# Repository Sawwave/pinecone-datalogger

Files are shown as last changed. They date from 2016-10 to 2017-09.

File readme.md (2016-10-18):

Arm based Datalogger running the Atmel SAM D20 MCU.

The Pinecone logger is a specialized, yet inexpensive data logger intended for sensing environmental variables. The ease of use and low cost of these datalogger systems make them ideal for mass deployment over a large area, allowing measurement of spatially-distributed data, rather than just a time-series of one point from a single logger.

The logger supports the following sensors natively:
	DHT-22 Temperature and Humidity sensor
	1 potentiometer implemented as a point dendrometer with 14 bits of precision
	multiple ports supporting sensors implementing the SDI-12 interface, which includes most Decagon brand sensors
	1 sap flow sensor implemented with a heating element and 4 thermocouples.

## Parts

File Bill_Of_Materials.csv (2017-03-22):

Digi-Key Part Number | Manufacturer | Manufacturer Part Number | Customer Reference | Quantity 1 | Quantity 2 | Quantity 3 | Mfg Std Lead Time | Description | Comments | RoHS Status | Lead Free Status | REACH Status
ATSAMD20E18A-AUTCT-ND | MICROCHIP TECHNOLOGY (VA) | ATSAMD20E18A-AUT | MCU | 1 | 0 | 0 | 19 Weeks | IC MCU 32BIT 256KB FLASH 32TQFP |  | RoHS Compliant | Lead free | Unaffected Dec-2015
DS3231SN#T&RCT-ND | MAXIM INTEGRATED (VA) | DS3231SN#T&R | RTC | 1 | 0 | 0 | 6 Weeks | IC RTC CLK/CALENDAR I2C 16-SOIC |  | RoHS Compliant | Lead free | Unaffected Jun-2016
AP2281-3WG-7DICT-ND | DIODES INCORPORATED (VA) | AP2281-3WG-7 | 3V3 LOAD SWITCH | 1 | 0 | 0 | 8 Weeks | IC LOAD SWITCH 100US SOT-26 |  | RoHS Compliant | Lead free | Unaffected Jun-2016
576-2749-1-ND | MICROCHIP TECHNOLOGY (VA) | MIC5211-LXYM6-TR | REGULATOR | 1 | 0 | 0 | 12 Weeks | IC REG LDO 3.3V/5V 80MA SOT23-6 |  | RoHS Compliant | Lead free | Unaffected Jun-2016
MAX4618ESE+-ND | MAXIM INTEGRATED | MAX4618ESE+ | TC MUX | 1 | 0 | 0 | 6 Weeks | IC MULTIPLEXER DUAL 4X1 16SOIC | Alternate Packaging Exists | RoHS Compliant | Lead free | Unaffected Jun-2016
MAX31856MUD+-ND | MAXIM INTEGRATED | MAX31856MUD+ | TC AMP | 1 | 0 | 0 | 14 Weeks | IC CONV THERMOCOUPLE 14TSSOP | Alternate Packaging Exists | RoHS Compliant | Lead free | Unaffected Jun-2016
CP-102A-ND | CUI INC | PJ-102A | PWR JACK | 1 | 0 | 0 | 10 Weeks | CONN PWR JACK 2X5.5MM SOLDER |  | RoHS Compliant | Lead free | Unaffected Jun-2015
952-1389-ND | HARWIN INC | M50-3600542 | CORTEX DEBUG PORT | 1 | 0 | 0 | 10 Weeks | CONN HDR 1.27MM SMD AU 10POS | Alternate Packaging Exists | RoHS Compliant | Lead free | Unaffected Dec-2015
ED10565-ND | ON SHORE TECHNOLOGY INC | OSTVN06A150 | 6 PIN TERM | 4 | 0 | 0 | 8 Weeks | CONN TERM BLOCK 2.54MM 6POS PCB |  | RoHS Compliant | Lead free | Unaffected Jun-2016
HR1964CT-ND | HIROSE ELECTRIC CO LTD (VA) | DM3AT-SF-PEJM5 | SD CARD PORT | 1 | 0 | 0 | 8 Weeks | CONN MICRO SD CARD PUSH-PUSH R/A | Multiple packaging options exist for the part number you requested. This part was selected by the Digi-Key Auto Sensor | RoHS Compliant | Lead free | Not Available
ED10567-ND | ON SHORE TECHNOLOGY INC | OSTVN10A150 | 10 PIN TERM | 1 | 0 | 0 | 8 Weeks | CONN TERM BLOCK 2.54MM 10POS PCB |  | RoHS Compliant | Lead free | Unaffected Jun-2016
490-1691-1-ND | MURATA ELECTRONICS (VA) | GRM21BR71C105KA01L | 1UF CAP | 2 | 0 | 0 | 11 Weeks | CAP CER 1UF 16V X7R 0805 |  | RoHS Compliant | Lead free | Unaffected Jun-2016
399-1170-1-ND | KEMET (VA) | C0805C104K5RACTU | 0.1UF CAP | 13 | 0 | 0 | 22 Weeks | CAP CER 0.1UF 50V X7R 0805 |  | RoHS Compliant | Lead free | Unaffected Jun-2016
490-4735-1-ND | MURATA ELECTRONICS (VA) | GRM219R61A106KE44D | 10UF CAP | 2 | 0 | 0 | 11 Weeks | CAP CER 10UF 10V X5R 0805 |  | RoHS Compliant | Lead free | Unaffected Jun-2016
399-1158-1-ND | KEMET (VA) | C0805C103K5RACTU | 0.01UF CAP | 2 | 0 | 0 | 22 Weeks | CAP CER 10000PF 50V X7R 0805 |  | RoHS Compliant | Lead free | Unaffected Jun-2016
399-9616-1-ND | KEMET (VA) | Z0805C221APMST | FERRITE BEAD | 1 | 0 | 0 | 18 Weeks | FERRITE BEAD 220 OHM 0805 1LN |  | RoHS Compliant | Lead free | Unaffected Jun-2016
785-1014-1-ND | ALPHA & OMEGA SEMICONDUCTOR INC (VA) | AO3420 | N-FET | 2 | 0 | 0 | 16 Weeks | MOSFET N-CH 20V 6A SOT23 |  | RoHS Compliant | Lead free | Unaffected Jun-2016
311-10KARCT-ND | YAGEO (VA) | RC0805JR-0710KL | 10K OHM | 8 | 0 | 0 | 22 Weeks | RES SMD 10K OHM 5% 1/8W 0805 |  | RoHS Compliant | Lead free | Unaffected Dec-2015
311-1.0KARCT-ND | YAGEO (VA) | RC0805JR-071KL | 1K OHM | 1 | 0 | 0 | 22 Weeks | RES SMD 1K OHM 5% 1/8W 0805 | Multiple packaging options exist for the part number you requested. This part was selected by the Digi-Key Auto Sensor | RoHS Compliant | Lead free | Unaffected Dec-2015
311-68ARCT-ND | YAGEO (VA) | RC0805JR-0768RL | 68 OHM | 1 | 0 | 0 | 22 Weeks | RES SMD 68 OHM 5% 1/8W 0805 | Multiple packaging options exist for the part number you requested. This part was selected by the Digi-Key Auto Sensor | RoHS Compliant | Lead free | Unaffected Dec-2015
475-2560-1-ND | OSRAM OPTO SEMICONDUCTORS INC(VA) | LY R976-PS-36 | LED | 1 | 0 | 0 | 10 Weeks | LED YELLOW DIFFUSED 0805 SMD |  | RoHS Compliant | Lead free | Unaffected Dec-2015
952-1662-1-ND | HARWIN INC (VA) | S8201-46R | BATT HOLDER | 1 | 0 | 0 | 10 Weeks | HOLDER BATT COIN 12.5X2.5MM SMD |  | RoHS Compliant | Lead free | Unaffected Dec-2015
P033-ND | PANASONIC - BSG | CR1220 | 3V BATT | 1 | 0 | 0 | 14 Weeks | BATTERY LITHIUM 3V COIN 12.5MM |  | Not applicable | Not applicable | Not Available

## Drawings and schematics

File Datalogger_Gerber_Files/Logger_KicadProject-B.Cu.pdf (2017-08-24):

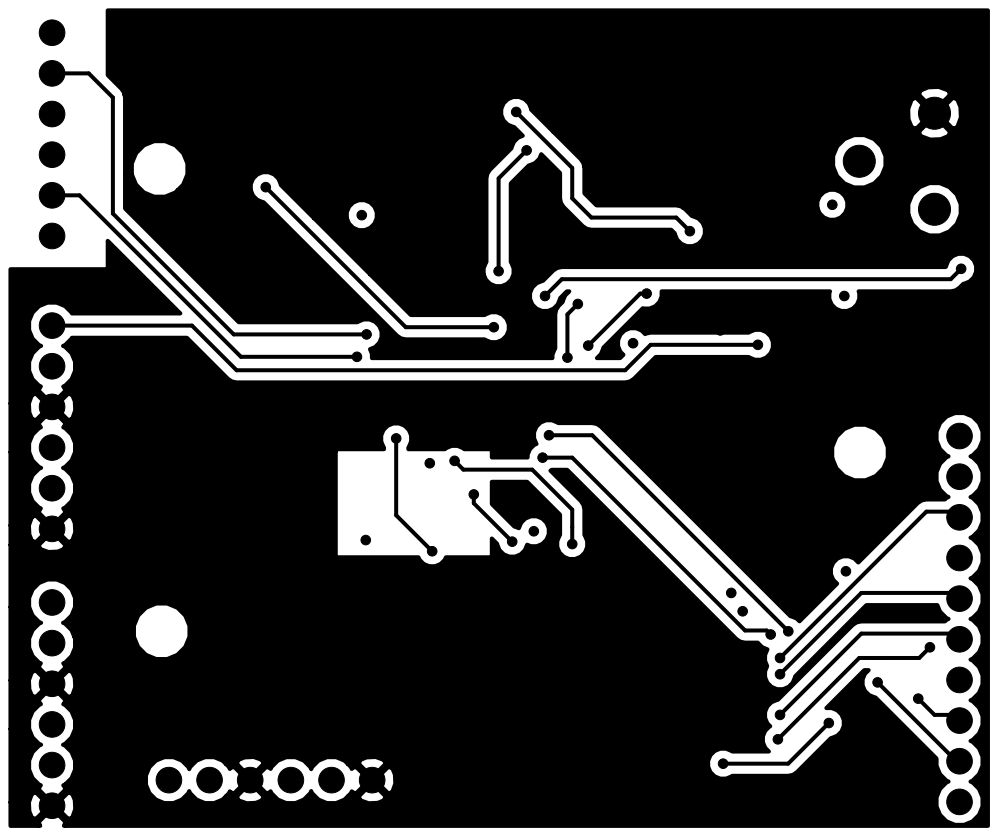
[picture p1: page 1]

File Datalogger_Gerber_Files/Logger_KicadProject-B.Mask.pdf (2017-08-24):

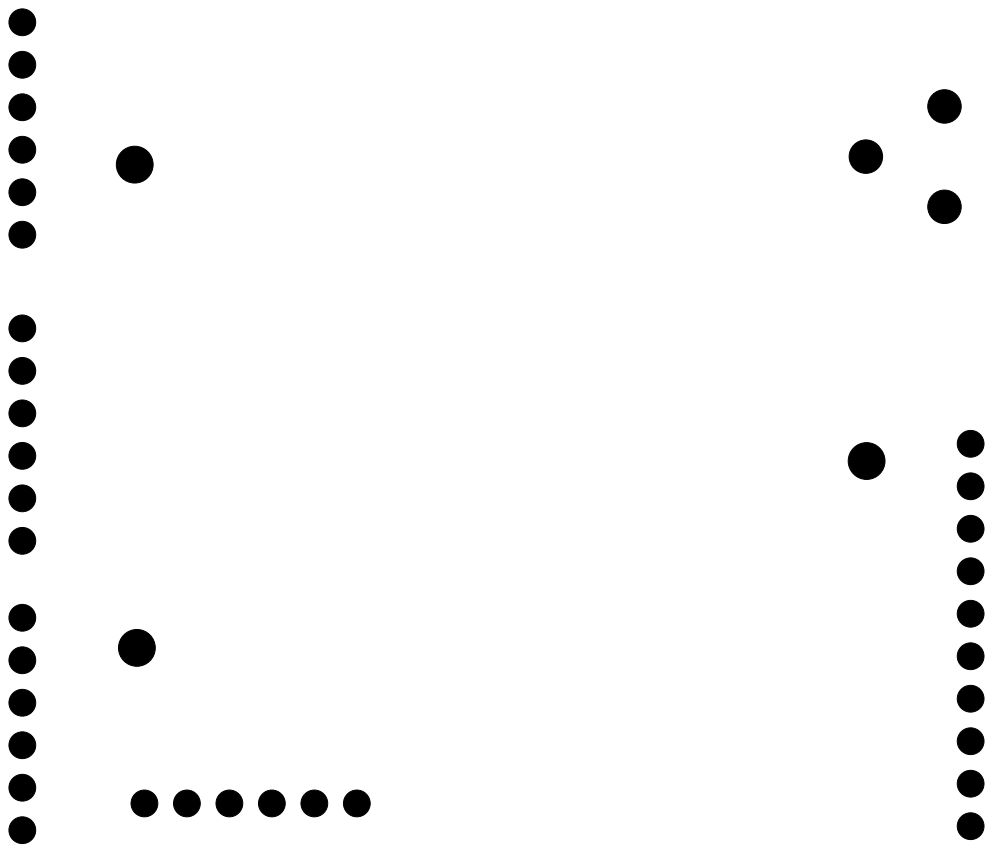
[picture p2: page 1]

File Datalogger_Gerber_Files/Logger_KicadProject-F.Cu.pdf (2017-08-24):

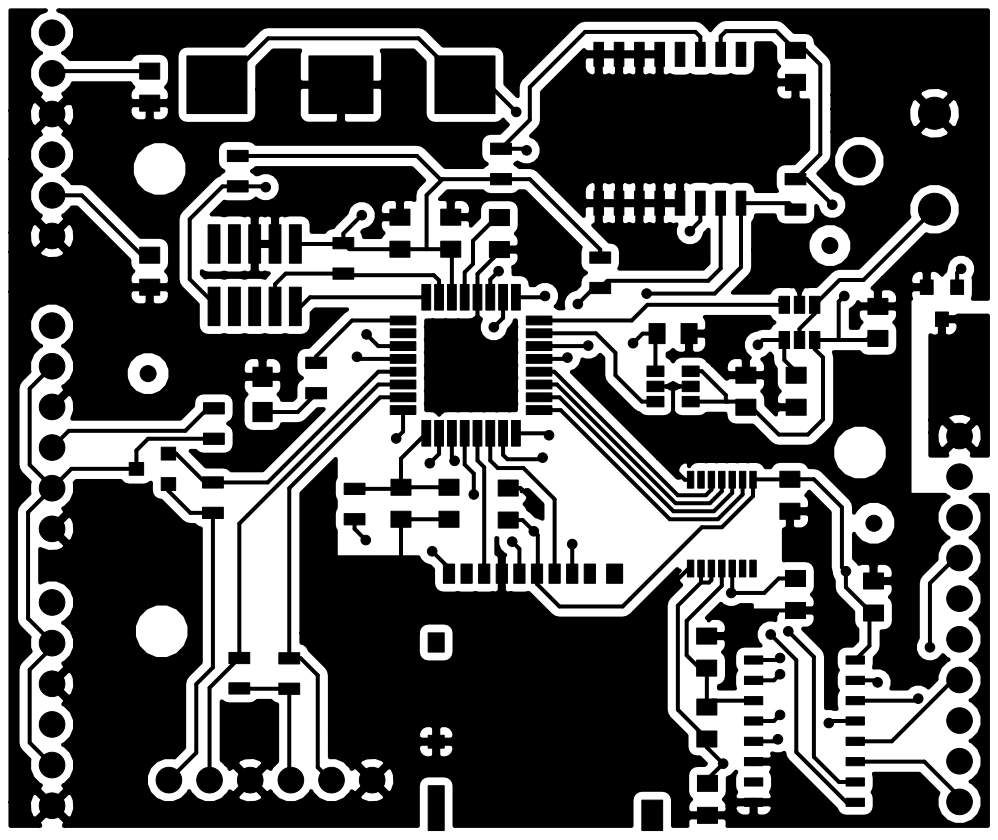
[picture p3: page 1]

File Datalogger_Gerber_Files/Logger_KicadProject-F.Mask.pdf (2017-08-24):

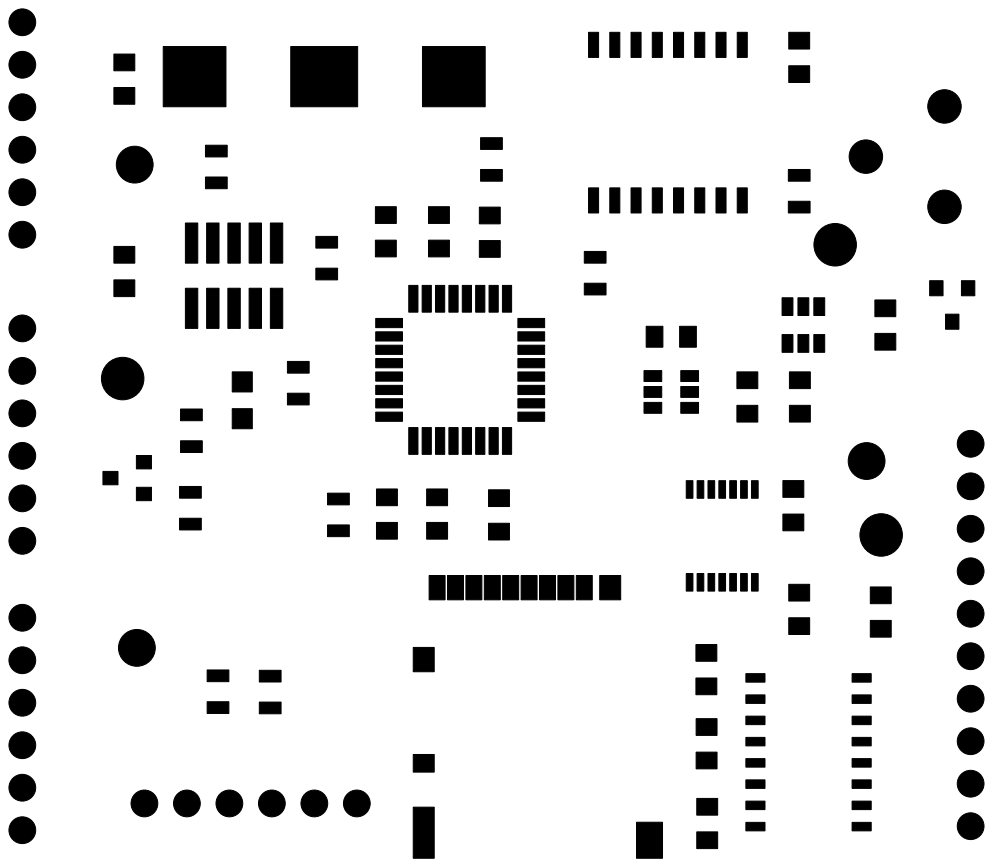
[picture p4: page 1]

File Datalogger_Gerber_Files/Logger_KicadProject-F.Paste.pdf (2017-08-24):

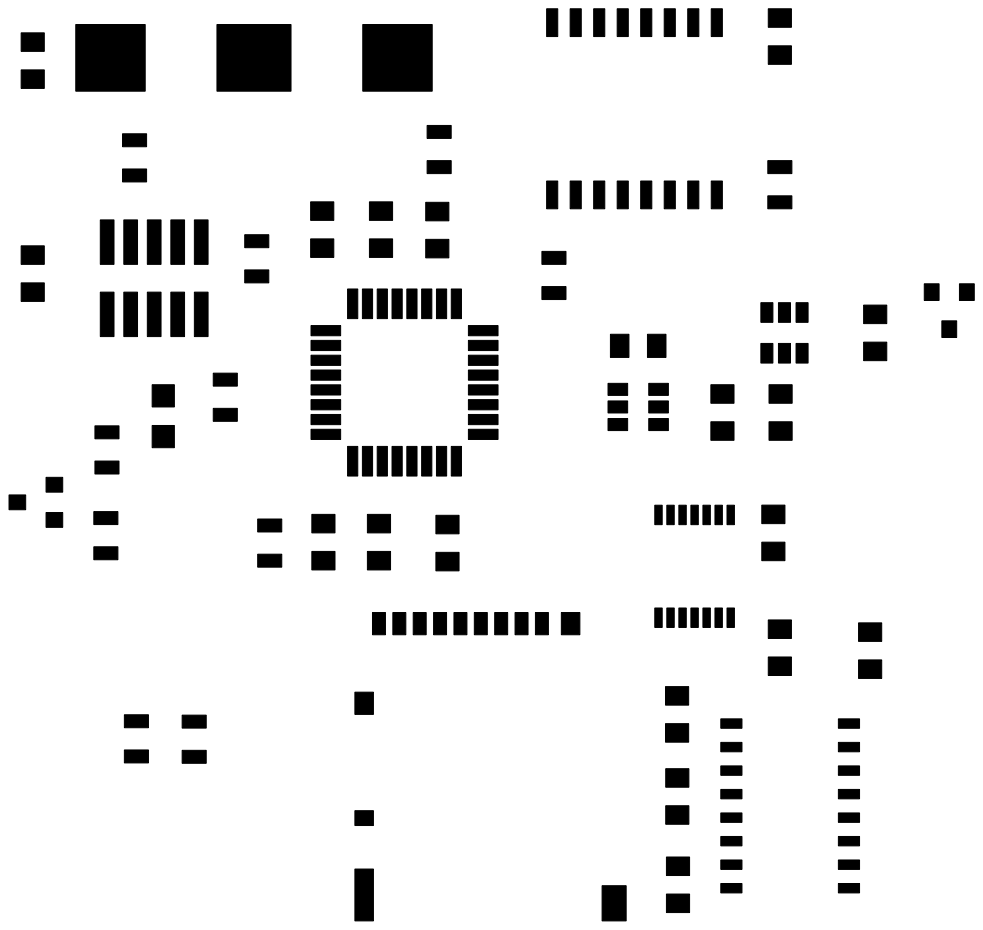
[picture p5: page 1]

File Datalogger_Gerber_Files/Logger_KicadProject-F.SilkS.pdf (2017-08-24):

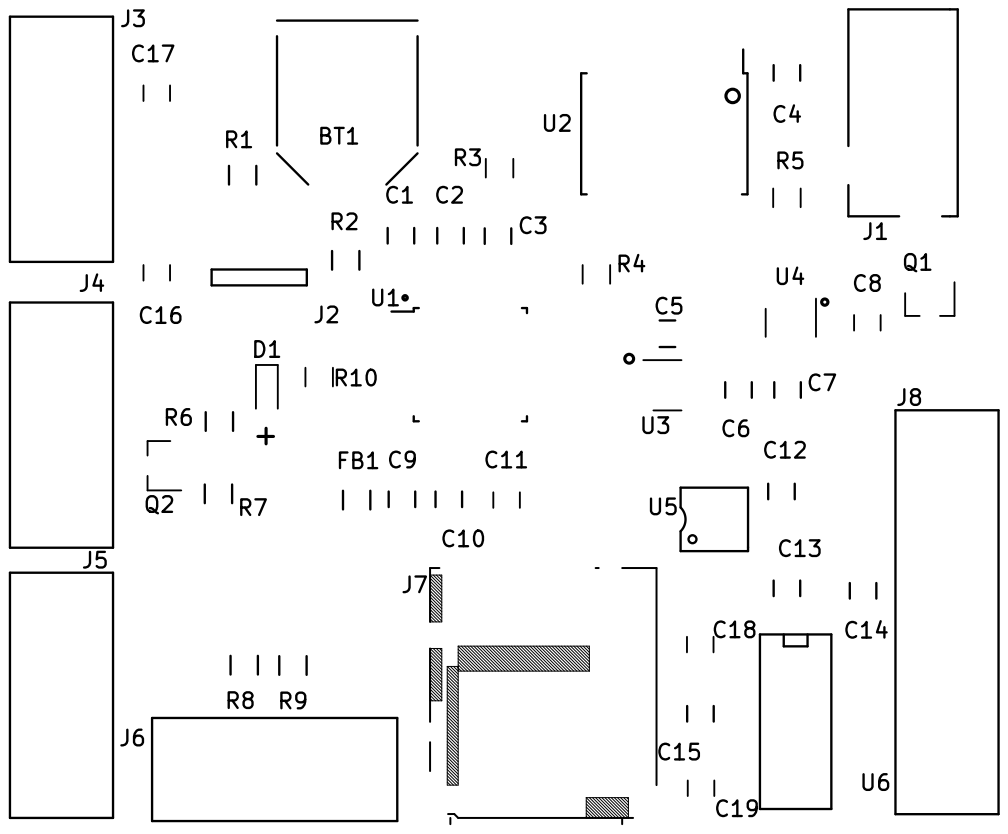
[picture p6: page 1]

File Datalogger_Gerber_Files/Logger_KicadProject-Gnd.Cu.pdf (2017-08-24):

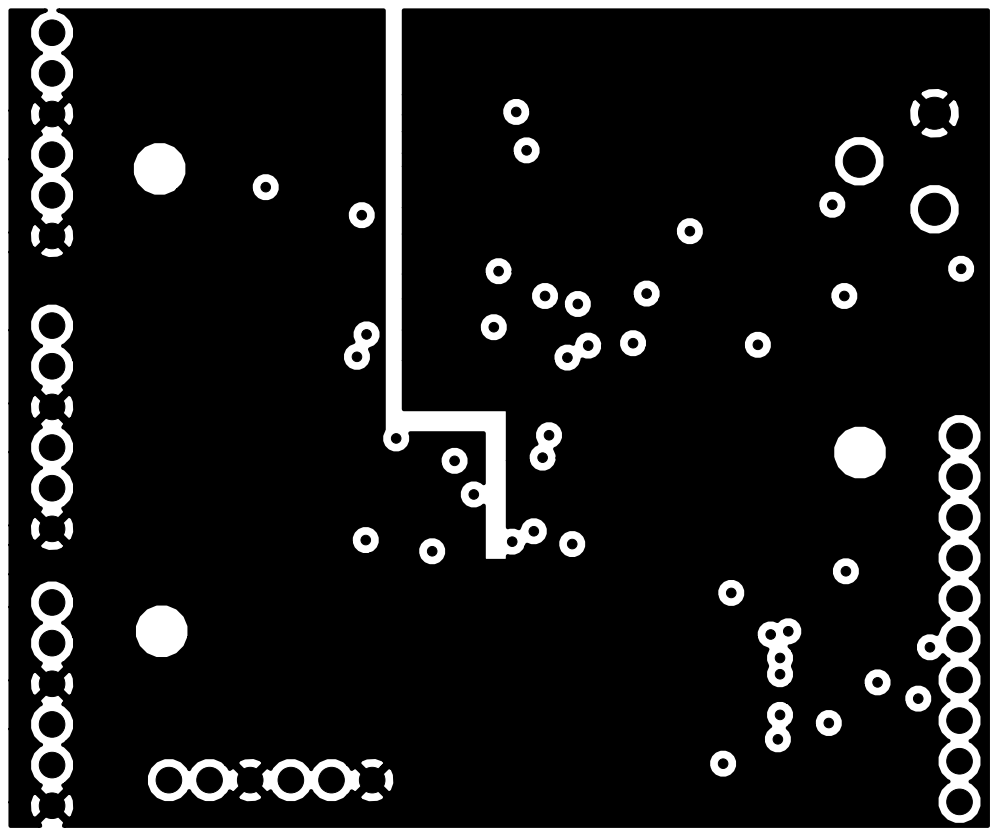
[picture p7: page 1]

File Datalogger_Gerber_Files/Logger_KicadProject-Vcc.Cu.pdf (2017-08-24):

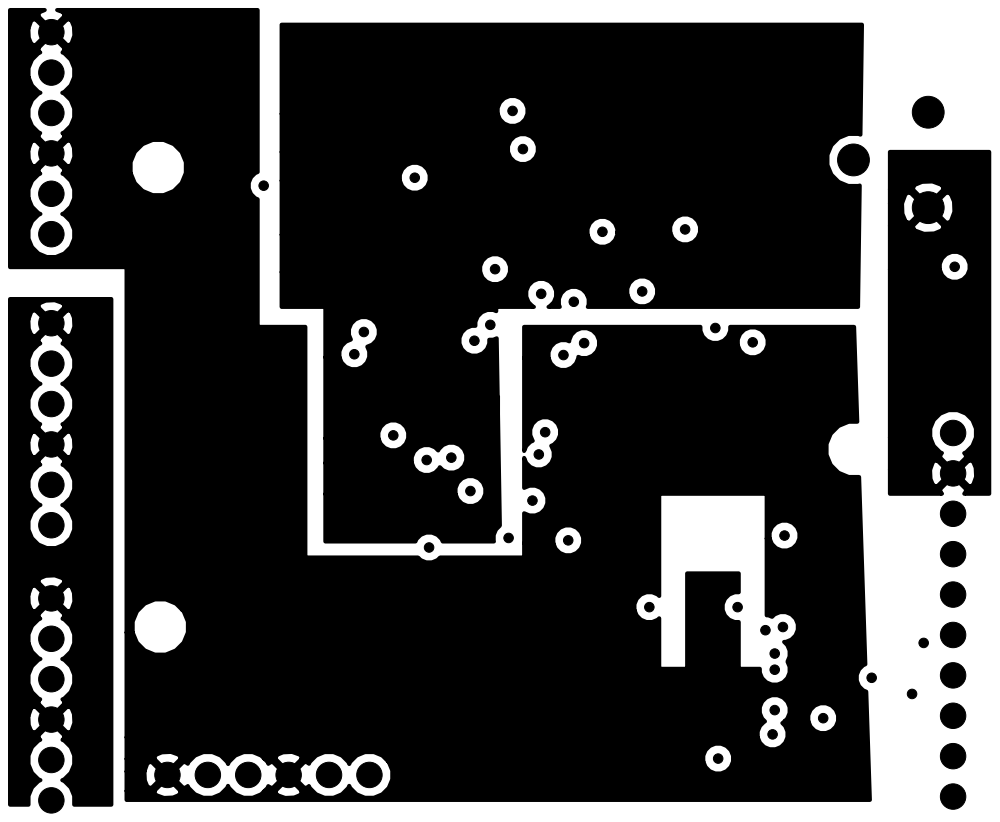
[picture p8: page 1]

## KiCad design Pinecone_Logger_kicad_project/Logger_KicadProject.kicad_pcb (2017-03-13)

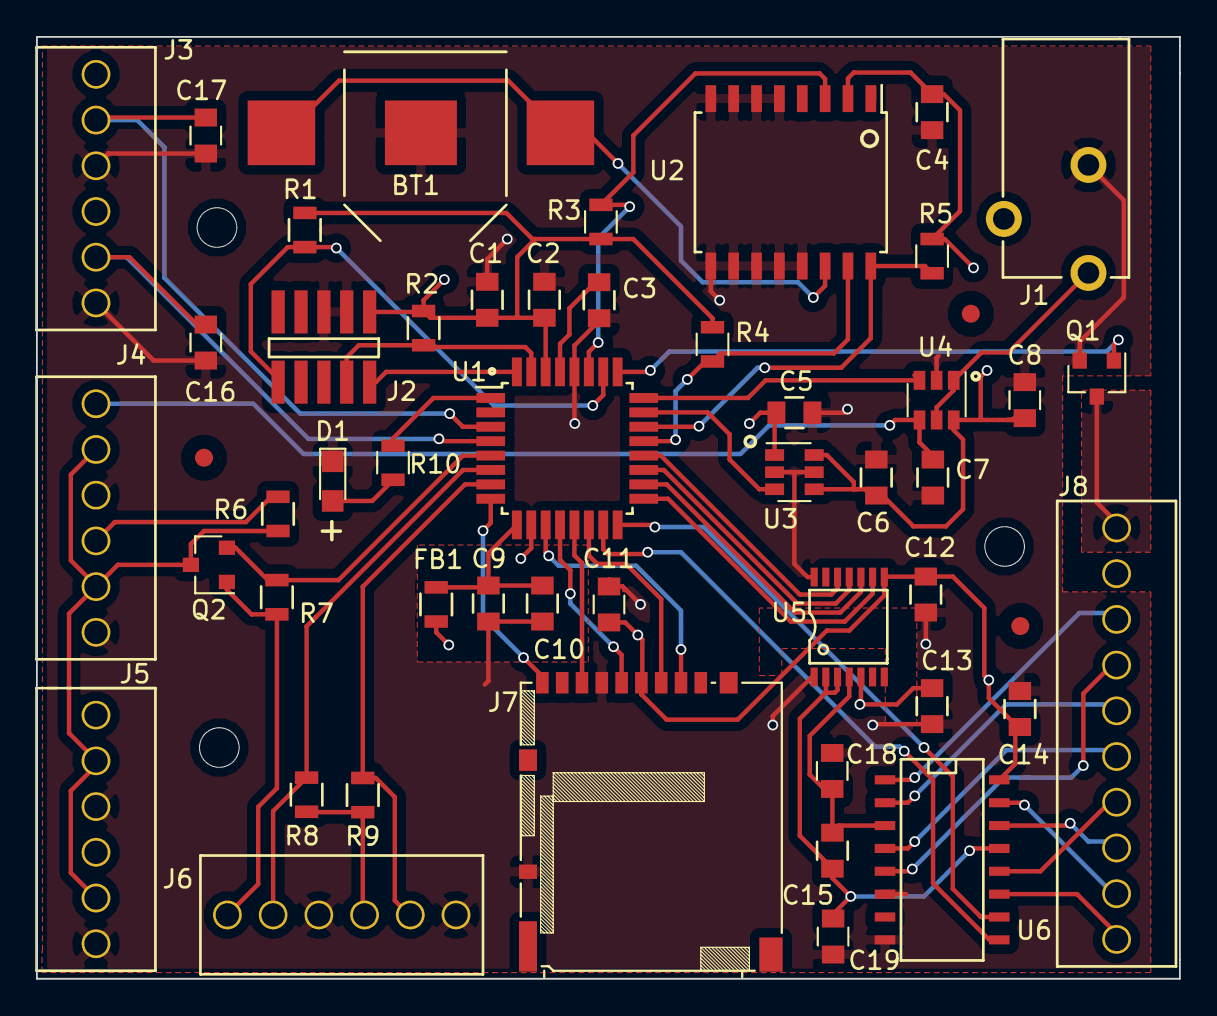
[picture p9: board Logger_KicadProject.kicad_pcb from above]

Board: 4 copper layers, 63.5 x 52.3 mm, 51 parts (0 on the bottom side), 47 nets.

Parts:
BT1: Battery; S8201R_Batt_Holder
C1, C10: GRM219R61A106KE44D; C_0805
C2, C4, C5, C7, C8, C9, C11, C12, C13, C14, C15, C16, C17: C0805C104K5RACTU; C_0805
C3, C6: GRM21BR71C105KA01L; C_0805
C18, C19: C0805C103K5RACTU; C_0805
D1: LY R976-PS-36; LED_0805
FB1: Z0805C221APMST; R_0805
FID1, FID2, FID3: Fiducial_1mm_Dia_2.54mm_Outer_CopperTop
J1: PJ-102A
J2: M50-3600542; 10_Pin_Cortex_SMD
J3, J4, J5, J6: OSTVN06A150; OSTVN06A150_6_Pin_Terminal
J7: DM3AT-SF-PEJM5; hirose-dm3at
J8: 10_Pin_Header; OSTVN10A150_10_pin_term
Q1, Q2: AO3420; SOT-23
R1, R3, R4, R5, R6, R7, R8, R9: RC0805JR-0710KL; R_0805
R2: RC0805JR-071KL; R_0805
R10: RC0805JR-0768RL; R_0805
U1: SAMD20E18A-A; TQFP-32_7x7mm_Pitch0.8mm
U2: DS3231; SOIC-16W_7.5x10.3mm_Pitch1.27mm
U3: AP2281; SOT-23-6
U4: MIC5211; SOT-23-6
U5: MAX31856; TSSOP-14
U6: MAX4618; SO-16-N

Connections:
3v3_PWR_ENABLE: U1.23, U3.3
5v_PWR_ENABLE: U1.24, U4.3
+3V3: C1.1, C2.2, C4.1, C6.1, C8.1, FB1.2, J2.1, R1.1, R2.1, R3.1, R4.1, R5.1, U1.30, U2.2, U3.4, U3.6, U4.6
+12V: J1.1, J8.2, U4.1, U4.5
DHT22_1: J6.2, R8.2, U1.6
DHT22_2: J6.5, R9.2, U1.7
DS3231_INTERRUPT: R3.2, U1.27, U2.3
DS3231_SCL: R5.2, U1.22, U2.16
DS3231_SDA: R4.2, U1.21, U2.15
Dend1: C17.1, J3.2, U1.3
Dend2: C16.1, J3.5, U1.4
GND: BT1.2, C1.2, C2.1, C3.2, C4.2, C5.2, C6.2, C7.2, C8.2, C9.1, C10.1, C11.1, C12.2, C13.2, C14.2, C16.2, C17.2, C18.2, C19.2, D1.1, J1.2, J2.2, J2.3, J3.3, J3.6, J4.3, J4.6, J5.3, J5.6, J6.3, J6.6, J7.6, J7.CD2, Q1.2, U1.10, U1.28, U2.5, U2.6, U2.7, U2.8, U2.9, U2.10, U2.11, U2.12, U2.13, U3.2, U3.5, U4.2, U5.1, U5.14, U6.6, U6.8
HEATER_ENABLE: Q1.1, U1.25
HEATER_SWITCHED_GND: J8.1, Q1.3
MAX31856_SERCOM_PAD0_MISO: U1.19, U5.11
MAX31856_SERCOM_PAD1_CS: U1.17, U5.9
MAX31856_SERCOM_PAD2_MOSI: U1.20, U5.12
MAX31856_SERCOM_PAD3_SCK: U1.18, U5.10
MUX_SEL_A: U1.16, U6.10
MUX_SEL_B: U1.15, U6.9
unnamed: BT1.1, U2.14
unnamed: C3.1, U1.29
unnamed: C9.2, C10.2, FB1.1, U1.9
unnamed: C15.1, C18.1, U5.4, U6.3
unnamed: C15.2, C19.1, U5.2, U5.3, U6.13
unnamed: D1.2, R10.2
unnamed: J4.2, J4.5, J5.2, J5.5, Q2.3, R6.2
unnamed: J8.3, U6.1
unnamed: J8.4, U6.5
unnamed: J8.5, U6.2
unnamed: J8.6, U6.4
unnamed: J8.7, U6.12
unnamed: J8.8, U6.14
unnamed: J8.9, U6.15
unnamed: J8.10, U6.11
RESET: J2.6, R1.2, U1.26
SDI_3v3_DATA: Q2.2, R7.2, U1.5
SD_CHIP_DETECT: J7.CD1, U1.8
SD_SERCOM_PAD0_MISO: J7.7, U1.13
SD_SERCOM_PAD1_CS: J7.2, U1.11
SD_SERCOM_PAD2_MOSI: J7.3, U1.14
SD_SERCOM_PAD3_SCK: J7.5, U1.12
STATUS_LED: R10.1, U1.1
SWDCLK: J2.9, R2.2, U1.31
SWDIO: J2.10, U1.32
SWITCHED_3v3: C5.1, C11.2, C12.1, C13.1, C14.1, J3.1, J3.4, J6.1, J6.4, J7.4, Q2.1, R7.1, R8.1, R9.1, U3.1, U5.5, U5.8, U6.16
SWITCHED_5v: C7.1, J4.1, J4.4, J5.1, J5.4, R6.1, U4.4

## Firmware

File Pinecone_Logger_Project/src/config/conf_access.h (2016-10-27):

/*****************************************************************************
 *
 * \file
 *
 * \brief Memory access control configuration file.
 *
 * This file contains the possible external configuration of the memory access
 * control.
 *
 * Copyright (c) 2009-2015 Atmel Corporation. All rights reserved.
 *
 * \asf_license_start
 *
 * \page License
 *
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
 * 3. The name of Atmel may not be used to endorse or promote products derived
 *    from this software without specific prior written permission.
 *
 * 4. This software may only be redistributed and used in connection with an
 *    Atmel microcontroller product.
 *
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
 * \asf_license_stop
 *
 ******************************************************************************/
/*
 * Support and FAQ: visit <a href="http://www.atmel.com/design-support/">Atmel Support</a>
 */


 //! Configuration of ctrl_access which is an abstraction layer for memory interfaces (common/services/storage/ctrl_access)

#ifndef _CONF_ACCESS_H_
#define _CONF_ACCESS_H_

#include "compiler.h"
//#include "board.h"


/*! \name Activation of Logical Unit Numbers
 */
//! @{
	#define LUN_0                DISABLE   //!< On-Chip Virtual Memory.
	#define LUN_1                DISABLE   //!< AT45DBX Data Flash.
	#define LUN_2                ENABLE    //!< SD/MMC Card over Slot 0
	#define LUN_3                DISABLE   //!< Spare
	#define LUN_4                DISABLE   //!< Spare
	#define LUN_5                DISABLE   //!< Spare
	#define LUN_6                DISABLE   //!< Spare
	#define LUN_7                DISABLE   //!< Spare
	#define LUN_USB              DISABLE   //!< Host Mass-Storage Memory.
//! @}

/*! \name LUN 0 Definitions
 */
//! @{
#define VIRTUAL_MEM                             LUN_0
#define LUN_ID_VIRTUAL_MEM                      LUN_ID_0
#define LUN_0_INCLUDE                           "virtual_mem.h"
#define Lun_0_test_unit_ready                   virtual_test_unit_ready
#define Lun_0_read_capacity                     virtual_read_capacity
#define Lun_0_unload                            NULL /* Can not be unloaded */
#define Lun_0_wr_protect                        virtual_wr_protect
#define Lun_0_removal                           virtual_removal
#define Lun_0_usb_read_10                       virtual_usb_read_10
#define Lun_0_usb_write_10                      virtual_usb_write_10
#define Lun_0_mem_2_ram                         virtual_mem_2_ram
#define Lun_0_ram_2_mem                         virtual_ram_2_mem
#define LUN_0_NAME                              "\"On-Chip Virtual Memory\""
//! @}

/*! \name LUN 1 Definitions
 */
//! @{
#define AT45DBX_MEM                             LUN_1
#define LUN_ID_AT45DBX_MEM                      LUN_ID_1
#define LUN_1_INCLUDE                           "at45dbx_mem.h"
#define Lun_1_test_unit_ready                   at45dbx_test_unit_ready
#define Lun_1_read_capacity                     at45dbx_read_capacity
#define Lun_1_unload                            NULL /* Can not be unloaded */
#define Lun_1_wr_protect                        at45dbx_wr_protect
#define Lun_1_removal                           at45dbx_removal
#define Lun_1_usb_read_10                       at45dbx_usb_read_10
#define Lun_1_usb_write_10                      at45dbx_usb_write_10
#define Lun_1_mem_2_ram                         at45dbx_df_2_ram
#define Lun_1_ram_2_mem                         at45dbx_ram_2_df
#define LUN_1_NAME                              "\"AT45DBX Data Flash\""
//! @}

/*! \name LUN 2 Definitions
 */
//! @{
#define SD_MMC_0_MEM                            LUN_2
#define LUN_ID_SD_MMC_0_MEM                     LUN_ID_2
#define LUN_2_INCLUDE                           "sd_mmc_mem.h"
#define Lun_2_test_unit_ready                   sd_mmc_test_unit_ready_0
#define Lun_2_read_capacity                     sd_mmc_read_capacity_0
#define Lun_2_unload                            sd_mmc_unload_0
#define Lun_2_wr_protect                        sd_mmc_wr_protect_0
#define Lun_2_removal                           sd_mmc_removal_0
#define Lun_2_usb_read_10                       sd_mmc_usb_read_10_0
#define Lun_2_usb_write_10                      sd_mmc_usb_write_10_0
#define Lun_2_mem_2_ram                         sd_mmc_mem_2_ram_0
#define Lun_2_ram_2_mem                         sd_mmc_ram_2_mem_0
#define LUN_2_NAME                              "\"SD/MMC Card Slot 0\""
//! @}

/*! \name LUN 3 Definitions
 */
//! @{
#define SD_MMC_1_MEM                            LUN_3
#define LUN_ID_SD_MMC_1_MEM                     LUN_ID_3
#define LUN_3_INCLUDE                           "sd_mmc_mem.h"
#define Lun_3_test_unit_ready                   sd_mmc_test_unit_ready_1
#define Lun_3_read_capacity                     sd_mmc_read_capacity_1
#define Lun_3_unload                            sd_mmc_unload_1
#define Lun_3_wr_protect                        sd_mmc_wr_protect_1
#define Lun_3_removal                           sd_mmc_removal_1
#define Lun_3_usb_read_10                       sd_mmc_usb_read_10_1
#define Lun_3_usb_write_10                      sd_mmc_usb_write_10_1
#define Lun_3_mem_2_ram                         sd_mmc_mem_2_ram_1
#define Lun_3_ram_2_mem                         sd_mmc_ram_2_mem_1
#define LUN_3_NAME                              "\"SD/MMC Card Slot 1\""
//! @}

/*! \name LUN 4 Definitions
 */
//! @{
#define SD_MMC_SPI_MEM                          LUN_4
#define LUN_ID_SD_MMC_SPI_MEM                   LUN_ID_4
#define LUN_4_INCLUDE                           "sd_mmc_spi_mem.h"
#define Lun_4_test_unit_ready                   sd_mmc_spi_test_unit_ready
#define Lun_4_read_capacity                     sd_mmc_spi_read_capacity
#define Lun_4_unload                            NULL
#define Lun_4_wr_protect                        sd_mmc_spi_wr_protect
#define Lun_4_removal                           sd_mmc_spi_removal
#define Lun_4_usb_read_10                       sd_mmc_spi_usb_read_10
#define Lun_4_usb_write_10                      sd_mmc_spi_usb_write_10
#define Lun_4_mem_2_ram                         sd_mmc_spi_mem_2_ram
#define Lun_4_ram_2_mem                         sd_mmc_spi_ram_2_mem
#define LUN_4_NAME                              "\"SD/MMC Card over SPI\""
//! @}

/*! \name LUN 5 Definitions
 */
//! @{
#define SD_MMC_MCI_0_MEM                        LUN_5
#define LUN_ID_SD_MMC_MCI_0_MEM                 LUN_ID_5
#define LUN_5_INCLUDE                           "sd_mmc_mci_mem.h"
#define Lun_5_test_unit_ready                   sd_mmc_mci_test_unit_ready_0
#define Lun_5_read_capacity                     sd_mmc_mci_read_capacity_0
#define Lun_5_unload                            NULL
#define Lun_5_wr_protect                        sd_mmc_mci_wr_protect_0
#define Lun_5_removal                           sd_mmc_mci_removal_0
#define Lun_5_usb_read_10                       sd_mmc_mci_usb_read_10_0
#define Lun_5_usb_write_10                      sd_mmc_mci_usb_write_10_0
#define Lun_5_mem_2_ram                         sd_mmc_mci_mem_2_ram_0
#define Lun_5_ram_2_mem                         sd_mmc_mci_ram_2_mem_0
#define LUN_5_NAME                              "\"SD/MMC Card over MCI Slot 0\""
//! @}

/*! \name USB LUNs Definitions
 */
//! @{
#define MEM_USB                                 LUN_USB
#define LUN_ID_MEM_USB                          LUN_ID_USB
#define LUN_USB_INCLUDE                         "uhi_msc_mem.h"
#define Lun_usb_get_lun()                       uhi_msc_mem_get_lun()
#define Lun_usb_test_unit_ready(lun)            uhi_msc_mem_test_unit_ready(lun)
#define Lun_usb_read_capacity(lun, nb_sect)     uhi_msc_mem_read_capacity(lun, nb_sect)
#define Lun_usb_read_sector_size(lun)           uhi_msc_mem_read_sector_size(lun)
#define Lun_usb_unload                          NULL
#define Lun_usb_wr_protect(lun)                 uhi_msc_mem_wr_protect(lun)
#define Lun_usb_removal()                       uhi_msc_mem_removal()
#define Lun_usb_mem_2_ram(addr, ram)            uhi_msc_mem_read_10_ram(addr, ram)
#define Lun_usb_ram_2_mem(addr, ram)            uhi_msc_mem_write_10_ram(addr, ram)
#define LUN_USB_NAME                            "\"Host Mass-Storage Memory\""
//! @}

/*! \name Actions Associated with Memory Accesses
 *
 * Write here the action to associate with each memory access.
 *
 * \warning Be careful not to waste time in order not to disturb the functions.
 */
//! @{
#define memory_start_read_action(nb_sectors)
#define memory_stop_read_action()
#define memory_start_write_action(nb_sectors)
#define memory_stop_write_action()
//! @}
/*! \name Activation of Interface Features
 */
//! @{
#define ACCESS_USB           false   //!< MEM <-> USB interface.
#define ACCESS_MEM_TO_RAM    true    //!< MEM <-> RAM interface.
#define ACCESS_STREAM        false   //!< Streaming MEM <-> MEM interface.
#define ACCESS_STREAM_RECORD false   //!< Streaming MEM <-> MEM interface in record mode.
#define ACCESS_MEM_TO_MEM    false   //!< MEM <-> MEM interface.
#define ACCESS_CODEC         false   //!< Codec interface.
//! @}

/*! \name Specific Options for Access Control
 */
//! @{
#define GLOBAL_WR_PROTECT    false //!< Management of a global write protection.
//! @}

/*! \name Sector size option for different storage media.
 */
//! @{
#define SECTOR_SIZE  512
//! @}

#endif  // _CONF_ACCESS_H_

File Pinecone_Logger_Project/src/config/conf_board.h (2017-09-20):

/**
* \file
*
* \brief User board configuration template
*
* Copyright (C) 2012-2015 Atmel Corporation. All rights reserved.
*
* \asf_license_start
*
* \page License
*
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
* 3. The name of Atmel may not be used to endorse or promote products derived
*    from this software without specific prior written permission.
*
* 4. This software may only be redistributed and used in connection with an
*    Atmel micro-controller product.
*
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
* \asf_license_stop
*
*/
/*
* Support and FAQ: visit <a href="http://www.atmel.com/design-support/">Atmel Support</a>
*/
#include "MAX31856/MAX31856.h"
#include <asf.h>
#ifndef CONF_BOARD_H
#define CONF_BOARD_H

#define DELETE_TIME_FILE_ON_SET 0	

#define SDI12_MAX_SUPPORTED_SENSORS 24
//#define BIT_TIMING_DELAY_CYCLES						955		//833us bit timing


// avoid PA30 and PA31, these are for SWCLK and SWDIO respectively
//Put all IN and OUT data GPIOs on the lower 16 pins to make WRCONFIG access easier.
//pins that are only OUT can be on the top 16

#define CONFIG_FLAGS_START_ON_HOUR		1 << 0
#define CONFIG_FLAGS_ENABLE_DEND_1		1 << 1
#define CONFIG_FLAGS_ENABLE_DEND_2		1 << 2
#define CONFIG_FLAGS_ENABLE_DHT_1		1 << 3
#define CONFIG_FLAGS_ENABLE_DHT_2		1 << 4
#define CONFIG_FLAGS_ENABLE_SDI			1 << 5
#define CONFIG_FLAGS_ENABLE_SAP_FLUX	1 << 6
#define CONFIG_FLAGS_DEFAULT		0xFF	//all flags on

struct LoggerConfig{
	char SDI12_SensorAddresses[SDI12_MAX_SUPPORTED_SENSORS + 3];	//extra chars on the end for ease of f_gets function.
	uint8_t SDI12_SensorNumValues[SDI12_MAX_SUPPORTED_SENSORS];
	uint8_t numSdiSensors;
	uint16_t loggingInterval;	//in minutes
	uint8_t thermocoupleType;
	uint8_t configFlags;
};



#define TIMED_SLEEP_TC_HARDWARE TC2
#define SDI12_TC_HARDWARE TC4



#define SD_VOLUME_NUMBER							0
#define SD_TIME_FILENAME							"0:time.txt"
#define SD_DATALOG_FILENAME							"0:data.csv"
#define SD_CONFIG_FILENAME							"0:lgr.cfg"

#define HEATER_TIMED_SLEEP_SECONDS					3

#ifdef USING_SAMD20XPLAINED

#define DHT22_1_PINMASK								1 << 8							// PIN_PA08
#define DHT22_2_PINMASK								1 << 9							// PIN_PA09
#define DHT22_ALL_PINMASK							DHT22_1_PINMASK | DHT22_2_PINMASK

#define SDI_PIN										PIN_PA10
#define SDI_PIN_PINMASK								1 << 10

#define DEND_ANALOG_PIN_1							ADC_POSITIVE_INPUT_PIN0			//PIN_PA02
#define DEND_PORT_PIN_1								PIN_PA02
#define DEND_ANALOG_PIN_2							ADC_POSITIVE_INPUT_PIN1			//PIN_PA03
#define DEND_PORT_PIN_2								PIN_PA03

#define DS1302_DATA_PIN_INDEX						11
#define DS1302_CLOCK_PIN_INDEX						12
#define DS1302_ENABLE_PIN_INDEX						28
#define DS1302_DATA_PINMASK							1 << DS1302_DATA_PIN_INDEX		//PIN_PA11
#define DS1302_CLOCK_PINMASK						1 << DS1302_CLOCK_PIN_INDEX		//PIN_PA12
#define DS1302_ENABLE_PINMASK						1 << DS1302_ENABLE_PIN_INDEX	//PIN_PA28
#define DS1302_ALL_PINMASK							 DS1302_DATA_PINMASK | DS1302_CLOCK_PINMASK | DS1302_ENABLE_PINMASK


#define MAX31856_THERMOCOUPLE_TYPE_USED				MAX31856_THERMOCOUPLE_TYPE_T
#define MAX31856_SPI_SERCOM_MODULE					SERCOM1
#define MAX31856_SPI_PINMUX_SETTING					SPI_SIGNAL_MUX_SETTING_E
#define MAX31856_SPI_PAD0							PINMUX_PA16C_SERCOM1_PAD0	//miso
#define MAX31856_SPI_PAD1							PINMUX_PA17C_SERCOM1_PAD1	//unused
#define MAX31856_SPI_PAD2							PINMUX_PA18C_SERCOM1_PAD2	//mosi
#define MAX31856_SPI_PAD3							PINMUX_PA19C_SERCOM1_PAD3	//sck
#define MAX31856_CS_PIN								PIN_PA17

#define SD_SERCOM_MODULE							SERCOM0
#define SD_PINMUX_SETTING							SPI_SIGNAL_MUX_SETTING_K	//chip detect on unused PA08, SCK, MISO, MOSI, and CD on PA0
#define SD_SPI_PIN0									PINMUX_PA04D_SERCOM0_PAD0	//chip detect
#define SD_SPI_PIN1									PINMUX_PA05D_SERCOM0_PAD1	//SCK
#define SD_SPI_PIN2									PINMUX_PA06D_SERCOM0_PAD2	//MISO
#define SD_SPI_PIN3									PINMUX_PA07D_SERCOM0_PAD3	//MOSI
#define SD_CS_PIN									PIN_PA14
#define SD_PIN_DETECT_LEVEL							0
#define SD_PIN_DETECT								PIN_PA11
#define SD_PIN_DETECT								PIN_PA11

//Mosfet PINS
#define SDI_DHT22_POWER_MOSFET_PINMASK				1 << 27	//PIN_PA24
#define HEATER_MOSFET_PINMASK						1 << 27	//PIN_PA25
#define DENDRO_TC_AMP_MOSFET_PINMASK				1 << 27	//PIN_PA27
#define SD_CARD_MOSFET_PINMASK						1 << 27	//PIN_PA28			
#define ALL_MOSFET_PINMASK							SDI_DHT22_POWER_MOSFET_PINMASK | HEATER_MOSFET_PINMASK | DENDRO_TC_AMP_MOSFET_PINMASK | SD_CARD_MOSFET_PINMASK

//TC Mux select
#define TC_MUX_SELECT_A_PINMASK						1 << 27 //PIN_PA22
#define TC_MUX_SELECT_B_PINMASK						1 << 27 //PIN_PA23
#define TC_MUX_SELECT_ALL_PINMASK					TC_MUX_SELECT_A_PINMASK | TC_MUX_SELECT_B_PINMASK


#else


#ifdef FIRST_PRINT_PINSET

#define DHT22_1_PINMASK								1 << 6							// PIN_PA07
#define DHT22_2_PINMASK								1 << 7							// PIN_PA08
#define DHT22_ALL_PINMASK							DHT22_1_PINMASK | DHT22_2_PINMASK

#define SDI_PIN										PIN_PA00
#define SDI_PIN_PINMASK								1 << 0

#define DEND_ANALOG_PIN_1							ADC_POSITIVE_INPUT_PIN4			//PIN_PA04
#define DEND_ANALOG_PIN_2							ADC_POSITIVE_INPUT_PIN5			//PIN_PA05
#define DENDROMETER_TRAVEL_DISTANCE_MICROMETERS		12700.0	//12.7 millimeters

#define MAX31856_THERMOCOUPLE_TYPE_USED				MAX31856_THERMOCOUPLE_TYPE_T

#define DS1302_DATA_PIN_INDEX						2
#define DS1302_CLOCK_PIN_INDEX						1
#define DS1302_ENABLE_PIN_INDEX						3
#define DS1302_DATA_PINMASK							1 << DS1302_DATA_PIN_INDEX		//PIN_PA02
#define DS1302_CLOCK_PINMASK						1 << DS1302_CLOCK_PIN_INDEX		//PIN_PA01
#define DS1302_ENABLE_PINMASK						1 << DS1302_ENABLE_PIN_INDEX	//PIN_PA03
#define DS1302_ALL_PINMASK							 DS1302_DATA_PINMASK | DS1302_CLOCK_PINMASK | DS1302_ENABLE_PINMASK
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

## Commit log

2016-10-18 Moved dendro travel distance to a board config macro
2016-10-25 finished createDataFileIfMissing, now queries sensors and creates headers appropriately
2016-10-31 added in MOSFET pin macros, created functionality to repair last line of data file. NEEDS TESTING
2016-11-01 changed file utils to close files immediately after done, since powering down when open may harm file(collapse?)
2016-11-02 added in main functionality to query sdi sensors.
2016-11-03 changed DS1302 to use PORTA instead of ASF GPIO fiddling, rearranged pin definitions in confboard to support SAM D20E
2016-11-04 added locality inforcement with static on local prototypes and globals in .c files
2016-11-14 added pin macros for using proto board v/ what they actual board will be
2016-11-29 removed SDI metadata command, since it's not supported by all sensors
2016-12-07 enabled Max31856 open-circuit detection
2016-12-14 fixed bug in parsing the SDI sensor number of values for more than 1 sensor.
2016-12-14 added kicad project
    [Logger_KicadProject.kicad_pcb, Logger_KicadProject.sch]
2016-12-20 created board schematic, BOM, PCB, and error checking required
    [Logger_KicadProject.sch]
2016-12-29 finished schematic design, created netlist
    [Logger_KicadProject.kicad_pcb, Logger_KicadProject.sch]
2017-01-04 pcb partially done, pushing to work remotely
    [Logger_KicadProject.kicad_pcb, Logger_KicadProject.sch]
2017-01-20 finished circuit design, firmware needs updating to respect pin changes
    [Logger_KicadProject.kicad_pcb, Logger_KicadProject.sch]
2017-01-20 added .pretty footprint libraries to the repo
    [Logger_KicadProject.kicad_pcb]
2017-01-20 created extended gerbers
    [Logger_KicadProject-B.Cu.gbr, Logger_KicadProject-B.Mask.gbr, Logger_KicadProject-B.SilkS.gbr, Logger_KicadProject-F.Cu.gbr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]
2017-01-24 touched up footprint
    [Logger_KicadProject.kicad_pcb]
2017-01-30 bunch of minor changes, changed DS1302 crystal to through hole with correst ESD
    [Logger_KicadProject-B.Cu.gbr, Logger_KicadProject-B.Mask.gbr, Logger_KicadProject-B.SilkS.gbr, Logger_KicadProject-F.Cu.gbr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]
2017-02-15 completed revision of circuit design, remapped pins in conf_board
    [Logger_KicadProject-B.Cu.gbr, Logger_KicadProject-B.Mask.gbr, Logger_KicadProject-B.SilkS.gbr, Logger_KicadProject-F.Cu.gbr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]
2017-02-15 fixed pin defines, added correct power mosfet transitions
2017-02-24 changed SOT-23 MOSFETS to have correct pinout. design should work with AO3420's now
    [Logger_KicadProject.kicad_pcb, Logger_KicadProject.sch]
2017-02-24 updated power jack footprint
    [Logger_KicadProject.kicad_pcb]
2017-02-24 changed schematic to use DS3231
    [Logger_KicadProject.sch]
2017-02-27 added MAX3231 to board, changed xlator mosfets to work
    [Logger_KicadProject.kicad_pcb, Logger_KicadProject.sch]
2017-03-03 Finished Logger V2 design, ready for pcb order
    [Logger_KicadProject.kicad_pcb, Logger_KicadProject.sch]
2017-03-09 logger circuit design finished, and ordered
    [Logger_KicadProject.kicad_pcb, Logger_KicadProject.sch]
2017-03-09 prototyped DS3231 functions
    [Logger_KicadProject-B.Cu.gbr, Logger_KicadProject-B.Mask.gbr, Logger_KicadProject-B.SilkS.gbr, Logger_KicadProject-Edge.Cuts.gbr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]
2017-03-13 updated schematic and pcb to correctly use SAM D20 E18, not the E16
    [Logger_KicadProject.csv, Logger_KicadProject.kicad_pcb, Logger_KicadProject.sch]
2017-03-21 added code for LED codes
2017-03-21 changed sd mount/init to have maximum attempts, and return success or failure
2017-03-21 changed sd init to repeat failure LED signal on fail
2017-03-21 implemented led status checking for config file existance
2017-03-21 added LedCodes folder
2017-03-21 fixed ReadConfigFile prototype return type
2017-03-21 included LedCodes in main because I am a derpus
2017-03-22 removed old testing filedws
    [Logger_KicadProject.csv]
2017-03-22 added BOM to repo
    [Pinecone_logger_1_2_BOM.csv, autoroute_test.kicad_pcb]
2017-03-22 LedCodes now sets LED to output for flashing, and back to input after for power saving
2017-03-22 changed SDI-12 to stay in input mode for power saving when not in use
2017-03-22 configured DHT IO pins to lower power mode when not in use
2017-03-22 TimedSleep now sets all gpio to power saving
2017-03-22 added LED pin to all gpio pinmask macro
2017-03-22 set all pins to low power mode before sleeping each loop
2017-03-22 set MAX4618 select pins to low power when not in use
2017-03-22 12v power mosfet now set to low power when not in use
2017-03-23 fixed MAX31856 CS pin macro
2017-03-23 finally fixed MAX31856, oh god
    [Logger_KicadProject.sch]
2017-04-20 SD card no longer wastes power through SERCOM bus
2017-04-20 added delay in SDI-12 response searching to allow for multiple sensors
2017-04-20 refactored i2c send/recieve for DS3231
    [Logger_KicadProject.sch]
2017-04-20 BOD on startup now wakes up for 1us to give detection time to check, just in case
2017-06-21 reorganized schematic, getting ready for publication
    [Logger_KicadProject.sch]
2017-07-10 changed heater pulse duration to 3 seconds to reflect Burgess et al
2017-08-24 Moved gerber files to a more prominent directory
    [Logger_KicadProject-B.Cu.gbr, Logger_KicadProject-B.Mask.gbr, Logger_KicadProject-B.SilkS.gbr, Logger_KicadProject-Edge.Cuts.gbr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]
2017-08-24 moved bill of materials to top level
    [Bill_Of_Materials.csv]
